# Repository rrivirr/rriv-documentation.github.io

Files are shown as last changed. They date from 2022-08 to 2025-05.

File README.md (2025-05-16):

# RRIV Documentation

### Introduction

RRIV is an open system for logging environmental data.

### Getting Started

* [Quick Start](quick_start.md)

### Organization

* [Goals](goals/)
* [Community](community/)
* [Licenses](licenses/)
* [Tools](organization/tools/)
* [Security](organization/security.md)

### Environmental Monitoring System

#### Platform

* [System Principles](principles/)
* [Features](features/)
* [Command Line Interface](cli/)

#### Applications

* [Build](build/)
* [Hardware Library](hardware-library/)
* [Kits](kits/)

### Engineering Organization

#### Development

* [Contributing](contributing/)
* [Roadmap](roadmap/)

#### System Documentation

* [Software Documentation](software/)
* [Hardware Documentation](hardware/)
* [Integrating Sensors and Actuators](integrating/)
* [Cloud](software/cloud.md)
* [Security](software/security.md)

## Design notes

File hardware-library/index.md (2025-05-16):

# Hardware Library

## Overview

The RRIV hardware library collects informations about various datalogger and sensor hardware that may be useful for specific environmental sensing use cases. TThird party sensors and other components may be easily integrated into the RRIV datalogger, and this library provides information to encourage that use. Documentation may also suggest particular sensor models, but these should not be interpreted as endorsements.

It is up to you to verify that any third party sensor or component will perform correctly for your specific deployment goals. Thus RRIV explicitly does not provide any warranty or guarentee for any third party hardware listed or suggested for use in our documentation.

Submissions to this hardware library are encouraged, and can be submitted as pull requests to this repository, located at https://github.com/rrivirr/rriv-documentation

## Sensors

* [Temperature](temperature/)
* [Conductivity](conductivity/)
* [pH](pH/)
* [Humidity](humidity/)
* [Color RGB](rgb/)
* [CO2](CO2/)
* [Methane](CO/)
* [CH4](ch4.md)

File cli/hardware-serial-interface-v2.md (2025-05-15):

# Hardware Serial Interface

## Overview

Command documentation conventions:

* \<required>
* \[optional]
* {...} json blob

RRIV compatible devices are configured using declarative commands as

`<command> <object> {key: value, key:value}`

or

`{command: <command>, object: <object>, key: value, key: value}`

Commands common to most objects are as follows:

### set

Creates or updates a resource.

### get

Gets current parameters of a resource, in a machine readable format.

### rm

Removes a resource

### reset

Resets parameters of an object back to defaults. Can accept a property to focus reset on that property.

### ls

Lists all resources of a particular tyle, in a tabular human readable format. This is not part of the standard, but implemented for ease of development. rrivctl does support this command, but by calling `get` and filtering the results down to a human readable format.

Consider if ls should be an abbreivate response for telemetry reasons, as in an index of objects without full properties.

### calibrate

Any object can potentially support a calibration routine

### run

Custom actions

\

## Commands

### Datalogger

Configurate data logger timing and metadata.

#### set datalogger {...}

{...} is JSON blob tha contains one or more datalogger parameter variables

```
{	
	"logger_name":"my device",
	"site_name":"OAK2:,
	"deployment_identifier":"X12",
	"interval": 10,
	"burst_number": 10,
	"start_up_delay": 1,
	"burst_delay": 2,
	"user_note": "none",
	"user_value": 12
}
```

| Parameter              | Data Type | Description                                                          |
| ---------------------- | --------- | -------------------------------------------------------------------- |
| logger\_name           | string    | a name for the logger                                                |
| site\_name             | string    | site code                                                            |
| deployment\_identifier | string    | identify a deployment                                                |
| wake\_interval         | int       | minutes between wakes while deployed                                 |
| warm\_up\_delay        | int       | minutes to wait between wakeup and measurement sensor initialization |
| burst\_interval        | int       | minutes between burst cycle initialization                           |
| user\_note             | string    | a note to add to each reading                                        |
| user\_value            | int       | a value to add to each reading                                       |

#### get datalogger \[{property: $property}]

* get datalogger \[property]

{command: get, object: datalogger, parameter: \<parameter>}

Get datalogger configuration. When called with a parameter argument, returns just the parameter requested. Otherwise returns the entire JSON blob.

#### reset datalogger \[{property: $property}]

* reset datalogger \[property]

Resets datalogger to factory default configuration, or just resets a particular property.

#### set datalogger {mode: \<mode\_request>, ...}

Changes the mode the datalogger is in

| Mode Request                               | Description                                                                                                       |
| ------------------------------------------ | ----------------------------------------------------------------------------------------------------------------- |
| interactive                                | Moves to interactive mode, which allows configuration                                                             |
| bench                                      | Moves to bench mode, which adds continuous serial output of measurements in addition to interactive mode features |
| deploy                                     | Moves immediately to deployment, sleeps the devices and awaits the next measurement cycle                         |
| deploy \<timestamp>                        | Moves to wait mode and sleeps the device. When timestamp is reached, the device wakes and deploys                 |

Datalogger also supports a shorthand which is outside the standard for mode switching over direct serial\
connection:

```
mode <mode_request>
```

\
\### Sensor

Commands to configure installed sensors.

#### set sensor \<id> {...}

Creates or updates a sensor configuration. If a sensor with the provided id is currently configured, it is updated. Otherwise, a new sensor configuration is created.

The JSON blob can contain some or all configuration parameters for indicated sensor driver. "type" specifies the kind of sensor installed and its corresponding driver, and is required when creating a new sensor.

Example (for generic analog sensor):

```
{	
	"type":"generic_analog",
	"burst_size":10,
	"adc_select":"internal",
	"sensor_port":1,
}
```

#### get sensor \[id] \[{property: }]

* rrivctl shorthand get sensor \[id] \[property]

Get a sensor configuration, corresponding to the id. When called with a parameter argument, returns just the parameter requested. Otherwise returns the entire JSON blob.

If id is not specified, returns a JSON array containing all sensor configurations.

get sensor also supports an aggregate property 'calibration' which returns all calibration parameters only

```
{
	'high_val': 5,
	'low_val': 2,
	'high_read': 2000,
	'low_read' : 300,
	'm': 2,
	'b': 0.2
}
```

#### rm sensor \<id>

Remove the sensor configuration matching the corresponding id

#### ls sensor

List all configured sensors in a tabluar format

#### calibrate sensor \<id> {action: $action, ...}

**action: point**

&#x20; Sets a calibration point

&#x20;`calibrate sensor <id> point {point: \$point_value, tag: $tag}`

**action: list, ls**

&#x20; Lists all the calibration points currently registered

&#x20;`calibrate sensor <id> list`

**action: remove, rm**

&#x20; Removes a registered calilbration point

&#x20;`calibrate sensor <id> remove {tag: $tag}`

**action: fit**

&#x20; Calculates fit based on calibration points that have been registered, and stores the fit.

&#x20;`calibrate sensor <id> fit { type: 'linear'}`

#### reset sensor {property: $property}

* reset sensor
* reset sensor {property: $property}
* reset sensor {property: 'calibration'}
* rrivctl shorthand: reset sensor $property

\
\### Actuator

Summary: actuator set, get, rm, ls

#### set actuator \[id] {...}

Creates or updates an actuator configuration. If an actuator with the provided id is currently configured, it is updated. Otherwise, a new sensor configuration is created.

#### get actuator \<id>

Get a actuator configuration, corresponding to the id. When called with a parameter argument, returns just the parameter requested. Otherwise returns the entire JSON blob.

If id is not specified, returns a JSON array containing all actuator configurations.

#### rm actuator \<id>

Remove the actuator configuration matching the corresponding id

#### ls actuator

List all configured actuators in a tabluar format

#### reset actuator {property: $property}

\
\### Telemeter

Summary: telemeter set, get, rm, ls

#### set telemeter \[id] {...}

Creates or updates an telemeter configuration. If an actuator with the provided id is currently configured, it is updated. Otherwise, a new sensor configuration is created.

#### get telemeter \<id> \[parameter]

Get a actuator configuration, corresponding to the id. When called with a parameter argument, returns just the parameter requested. Otherwise returns the entire JSON blob.

If id is not specified, returns a JSON array containing all telemeter configurations.

#### rm telemeter \<id>

Remove the telemeter configuration matching the corresponding id

#### ls telemeter

List all configured telemeters in a tabluar format

#### reset telemeter {property: $property}

\
\### Board\
The commands access features of the board itself and firmware metadata

This consists of three types of commands

* get/set commands in the standard that report hardware properties.
* warranty/license shorthands for human operators on the serial connection
* debugging shorthands for human developers on the serial connection

This is a custom namespace at the top level.

#### board version

```
get board { property: 'version'}
```

rrivctl: get board version

#### board firmware warranty

```
get board { property: 'firmware-warranty'}
get board { property: 'firmware'}
```

#### board firmware conditions

#### board firmware license

#### board rtc set \<epoch>

```
set board {'epoch': \$epoch} 
```

Set real time clock epoch time

#### board rtc get

Get the current real time clock epoch time stored on a RRIV device

```
get board { property: 'epoch'}
```

#### board restart

```
run board {'commmand' : 'restart'}
```

#### board i2c ls

#### board memory check

#### board mcu \[stop,sleep]

#### board signal \[high,low]

| Signal   | Description                        |
| -------- | ---------------------------------- |
| exADC    | enable/disable exADC               |
| 3v3Boost | enable/disable 3v3 boost converted |

\
\### Device\
Top level commands that dump and load all for the device in one payload

#### get

#### set

#### reset \<STM\_ID>

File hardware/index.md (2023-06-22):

# Hardware Documentation

## Overview

## Resources

* [Datasheets](datasheets/)
* [STLink Interface](board/programming-interface.md)

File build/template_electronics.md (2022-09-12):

# Electonics Build for ... 

## Bill of Materials

| Item        | Quantity    | Source URL  |
| ----------- | ----------- | ----------- |
| Waterbear   | 1           | https://... |
| Nucleao     | 1           | https://... |

## Schematics

Wiring diagrams.

## Build Process

### Tools & Skills

What's needed to build.

### Parts Fabrication

What to do with the bill of materials.

### Assembly & Waterproofing

How to put it together.

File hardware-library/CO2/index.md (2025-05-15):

# Carbon Dioxide (CO2) Sensors

## Background Science

* https://agupubs.onlinelibrary.wiley.com/doi/full/10.1002/2016RG000547

## Atlas Scientific CO2 Sensor

### Sensor Details

technology: optical\
range: 0-10000ppm +/-50ppm\

### RRIV Integration Details

driver: atlas\_co2\
case: developed\

### Product Links

* [Product page](index.md)

### Datasheets

* [Archived technical info 2023-07-07](index.md)

## MH-Z16

### Sensor Details

technology: NDIR\
range: 0-100000ppm\

### RRIV Integration Details

driver: under development\
case: under development\

### Product Links

* [Product page](https://sandboxelectronics.com/?product=100000ppm-mh-z16-ndir-co2-sensor-with-i2cuart-5v3-3v-interface-for-arduinoraspeberry-pi)
* [Datasheet](https://sandboxelectronics.com/wp-content/uploads/2018/08/Z16DS.pdf)

## Adafruit SCD41

### Sensor Details

technology: photoacoustic\
range: 400-5000ppm +/-50ppm\

### RRIV Integration Details

driver: not developed\
case: not developed\

### Product Links

* [Product page](https://www.adafruit.com/product/5190)

## Adafruit SCD30

### Sensor Details

technology: NDIR\
range: 400-10,000ppm +/-30ppm\

### RRIV Integration Details

driver: not developed\
case: not developed\

### Product Links

* [Product page](https://www.adafruit.com/product/4867)

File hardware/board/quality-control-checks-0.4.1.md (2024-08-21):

# Quality Control Checklist

## Checklist
* [pass] Powers up over USB
* [pass] Programmable
* [pass] Serial
* [pass] RGB LED
* [mod] Switchable power cycling
* [pass] 2.4V boost converter
* [pass] 3.3V boost converter
* [pass] 5V boost converter
* [pass] VIN measure
* [pass] intADC
* [pass] exADC
* [ ] I2C 3.3V
* [pass] I2C 5V
* [pass] exADC MOSFET
* [pass] Battery level MOSFET 
* [pass] intADC MOSFET
* [ ] Wake switch
* [mod] Voltage ORing VDD
* [pass] Voltage ORing 3.3V

## Noted Defects
* Orientation of reset button still wrong
  * Mitigation: remove reset button	
  * Alternate: may be possible to disconnect pads diagonally and get intended functionality
* Switchable power cycling resets on set low
  * Root cause: both ideal diodes are turning off at threshold
  * Mitigation: replace R21 with 357K
  * Fix: use mitigation or use ST pin on ideal diode for synchronized switching
* i2c hangs
  * this appears to be due to going low when 3v3 is switch off.
  * Fix: pullups should be agains VDD, not 3V3 

## Other Notes
* When VIN measure is disable, the ADC still reads a nonzero value
  * Suspect this is a floating voltage, test using current meter
* 5V boost has a very limited swing, around 100mV.  Still, the ripple pattern is spiky.  We could add a ferrite bead to smooth it.  This could go in the place of SB27 to feed the the exADC with smooth 5v.  To feed i2c we could place a bead in a similar solder bridge location.
* BOM included wrong pin count socket for J11 and J12

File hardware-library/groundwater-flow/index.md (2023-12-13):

# Data Sheets
* https://www.mouser.com/datasheet/2/609/max30210-3128806.pdf
* https://www.mouser.com/pdfDocs/max30210evkit.pdf
* https://www.analog.com/media/en/technical-documentation/data-sheets/4316fa.pdf

BOM
* https://www.ti.com/lit/ds/symlink/tps7a20.pdf?HQS=dis-dk-null-digikeymode-dsf-pf-null-wwe&ts=1702470498525

# Other Temperature Sensors
* https://www.te.com/usa-en/product-CAT-DTS0001.html
* https://www.harfington.com/products/p-1213532?currency=USD&variant=42565797216505&utm_medium=cpc&utm_source=google&utm_campaign=Google%20Shopping&stkn=f8e35277684b&utm_source=google&utm_medium=cpc&utm_campaign=1013-pmax-us-powerele8-&utm_term=1013-pmax-us-powerele8-&utm_content=ywh&gad_source=1&gclid=Cj0KCQiA35urBhDCARIsAOU7Qwlhizj8V51s7NARGC8W3OzX_mQPplGzPusJnYH1U20nPWnSQYRO4ssaAhsTEALw_wcB

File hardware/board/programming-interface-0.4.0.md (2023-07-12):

# Programming Interface

## Overview

This document details the programming interface for version 0.4.0 of the RRIV datalogger.  For version 0.4.1 and later, see [programming-interface.md]()

On version 0.4.0 of the RRIV datalogger, the ST-Link programming pins and serial interface pin are exposed in J5 and J6.  

These locations may have pin headers or JST XH size sockets installed, but either will accept Dupont connectors from the corresponding pins on the programming board.  This is the preferred way to interface with and program the MCU.

## Boards and Locations
### RRIV PCB
RRIV PCB

### RRIV PCB Layout
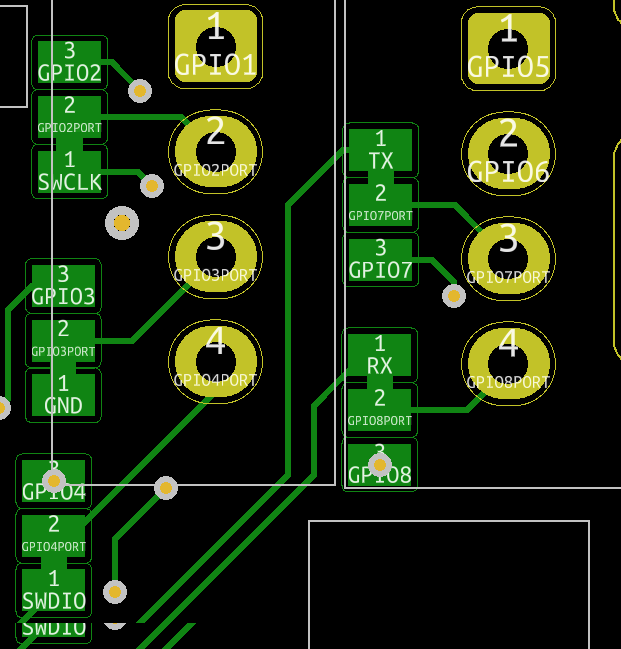
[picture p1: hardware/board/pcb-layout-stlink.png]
RRIV PCB Layout


### Programming Board
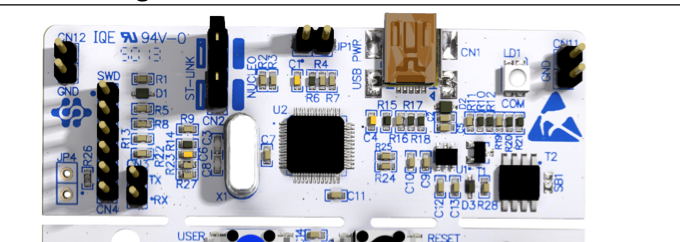
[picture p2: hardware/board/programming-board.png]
Programming Board


### Programming Board Detail
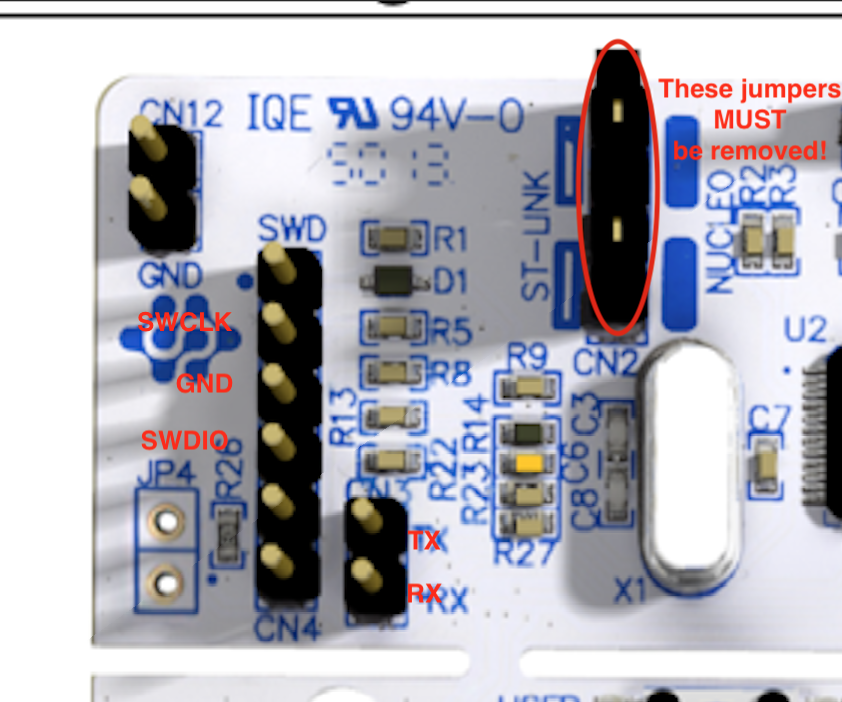
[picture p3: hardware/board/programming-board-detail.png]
Programming Board


### Programming Board Pinout
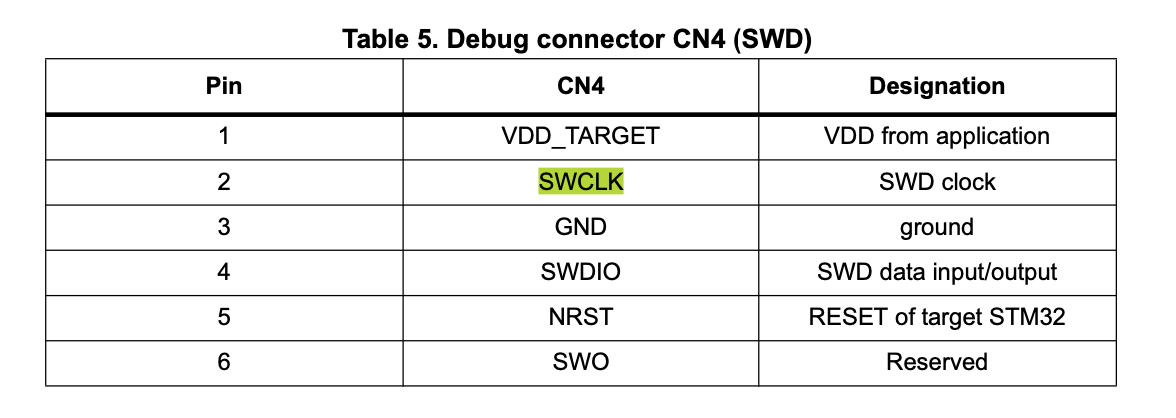
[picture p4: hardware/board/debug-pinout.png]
Programming Board


## Connecting the RRIV datalogger for programming

1. Connect SWCLK, GND, SWDIO, RX, and TX from the programming board ot the RRIV datalogger using Dupont female-female connectors
2. Ensure that both jumpers at CN2 on the programmer board are removed
2. Plug the USB port of the programming board into the computer using a USB cable.
3. Power the RRIV board, using a second USB cable into the RRIV datalogger's USB port. (v0.4.1 boards may also be powered by battery)
4. You may now program the RRIV datalogger and monitor serial using platformio.

## Notes
* The USB port on the RRIV datalogger currently in ONLY for supplying power to the board on the bench.  The RRIV datalogger cannot currently be programmed or interacted with thorugh this port.
* In some cases the MCU on the RRIV datalogger may need to be reset in order to program it.  The recommended path for this is to power cycle the board.

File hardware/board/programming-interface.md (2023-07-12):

# Programming Interface

## Overview

On version 0.4.1 and later of the RRIV datalogger, the ST-Link programming pins and serial interface pin are exposed in J5 and J6.  

These locations may have pin headers or JST XH size sockets installed, but either will accept Dupont connectors from the corresponding pins on the programming board.  This is the preferred way to interface with and program the MCU.

## Boards and Locations
### RRIV PCB
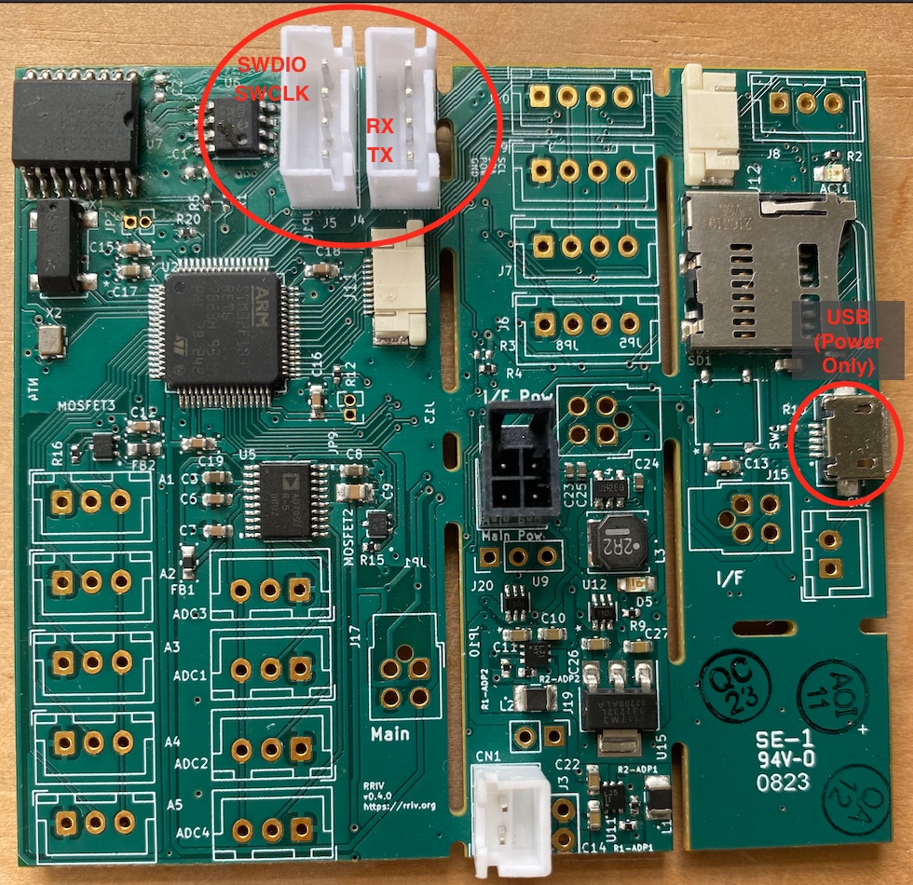
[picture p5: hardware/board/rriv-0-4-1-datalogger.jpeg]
RRIV PCB


### Programming Board
Programming Board

### Programming Board Detail
Programming Board

### Programming Board Pinout
Programming Board

## Connecting the RRIV datalogger for programming

1. Connect SWCLK, SWDIO, RX, and TX from the programming board ot the RRIV datalogger using Dupont female-female connectors
2. Power the board using USB. Generally if the board is powered by USB, it is not necessary to connect an additional ground cable between the programming board and the PCB
3. Ensure that both jumpers at CN2 on the programmer board are removed
4. Plug the USB port of the programming board into the computer using a USB cable.
5. Power the RRIV board, using a second USB cable into the RRIV datalogger's USB port. (v0.4.1 boards may also be powered by battery)
6. You may now program the RRIV datalogger and monitor serial using platformio.
7. If the board fails to program, the following two additional steps may help it get into programming mode
  1. Connect a Dupont cable between GND on the programmer one of the GND pins on the RRIV datalogger.  Typically you may use the GND pin on an open I2C socket.
  2. Press the reset button just before the board is programmed.  You may do this immediately before or immediately after pressing the 'run' button in platformIO.

## Notes
* The USB port on the RRIV datalogger currently in ONLY for supplying power to the board on the bench.  The RRIV datalogger cannot currently be programmed or interacted with through this port.
* In some cases the MCU on the RRIV datalogger may need to be reset in order to program it.  The recommended path for this is to power cycle the board.

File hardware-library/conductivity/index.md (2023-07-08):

# Electical Conducitivity Sensors

## Atlac EC Sensor

### RRIV Driver Details
driver: atlas_ec

### Product Links
* [Product page](https://www.google.com/url?sa=t&rct=j&q=&esrc=s&source=web&cd=&ved=2ahUKEwi30oOe7P3_AhVPJkQIHbI7B8wQjBB6BAgXEAE&url=https%3A%2F%2Fatlas-scientific.com%2Fkits%2Fconductivity-k-0-1-kit%2F&usg=AOvVaw3qBv8ugVFJyb1ZsS51Sytv&opi=89978449)

### Datasheets
* [Archived technical info 2023-07-07]()

## DIY EC Sensor
under development

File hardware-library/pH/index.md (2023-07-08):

# pH Sensors

## Gravity Analog ph Sensor

### RRIV Driver Details
driver: generic_analog

### Product Links
* [Product page](https://www.dfrobot.com/product-1782.html)
* [Product wiki](https://wiki.dfrobot.com/Gravity__Analog_pH_Sensor_Meter_Kit_V2_SKU_SEN0161-V2)

### Datasheets
* [Archived technical info 2023-07-07](Gravity__Analog_pH_Sensor_Meter_Kit_V2_SKU_SEN0161-V2-DFRobot.pdf)

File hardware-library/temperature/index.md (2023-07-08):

# Temperature Sensors

## Basic Analog Temperature Sensor (Thermistor)

This DIY implementation involves wiring a thermistor into a voltage divider to produce an analog sensor.

### RRIV Driver Details
driver: generic_analog

### Product Links

### Datasheets

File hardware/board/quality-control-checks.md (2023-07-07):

# Quality Control Checklist

[ ] Powers up over USB
[ ] RGB LED
[ ] 2.4V boost converter
[ ] 3.3V boost converter
[ ] 5V boost converter
[ ] Switchable power from battery
[ ] intADC
[ ] exADC
[ ] I2C 3.3V
[ ] I2C 5V
[ ] exADC MOSFET
[ ] Battery level MOSFET 
[ ] intADC MOSFET
[ ] Wake switch

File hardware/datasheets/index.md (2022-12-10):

# Datasheets

## Overview

This folder contains datasheets for components of the WaterBear and RRIV PCBs

## Datasheets
* [F103RB MCU](stm32f103rb.pdf)
* [F103RB MCU Reference Manual.pdf](STM32F10xxx%20Reference%20Manual.pdf)
* [EEPROM](24AA08-24LC08B-24FC08-8K-I2C-Serial-EEPROM-20001710N.pdf)
* [External ADC](AD7091R-5.pdf)
* [Boost Converter](ADP1606_ADP1607.pdf)
* [RGB LED](APHF1608LSEEQBDZGKC.pdf)
* [Realtime Clock](DS3231.pdf)
* [Nucleo User Manual](Nucleo64%20User%20Manual.pdf)
* [Nucleo Schematics](Nucleo%20F103RB%20Schematics.pdf)

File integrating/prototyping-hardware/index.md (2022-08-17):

# Recommended process for prototyping hardware

1. Design a strip based routing for the circuit
1. Layout circuit on breadboard
  * Connect nets using strip based routing
  * Use plugs to connect other components
1. Transfer circuit to stripboard for deployment

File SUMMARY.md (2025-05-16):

# Table of contents

* [RRIV Documentation](README.md)
* [Quick Start](quick_start.md)
* [applications](applications/README.md)
  * [DF Robot Analog pH Sensor](applications/dfrobot_ph_integration.md)
  * [GHG Bucket Flux Protocol](applications/ghg_flux_method.md)
* [build](build/README.md)
  * [Waterproof CO2 Sensor](build/co2_sensor.md)
  * [Electonics Build for R\&D Conductivity Sensor](build/conductivity_sensor_switching.md)
  * [Build](build/index.md)
  * [Methane and Carbon Dioxide Case](build/methane_case_1ft.md)
  * [GHG System Case](build/methane_case_2ft.md)
  * [Waterproof Methane Sensor](build/methane_sensor.md)
  * [Case Title](build/template_case.md)
  * [Electonics Build for ...](build/template_electronics.md)
  * [Sensor Title](build/template_sensor.md)
  * [applications](build/applications/README.md)
    * [RRIV Methane Beta Setup](build/applications/methane_beta_build.md)
  * [sensors](build/sensors/README.md)
    * [DF Robot Analog pH Sensor](build/sensors/dfrobot_ph_integration.md)
* [cli](cli/README.md)
  * [CLI commands](cli/CLI_commands_v1.md)
  * [RRIVCTL Sugars](<cli/RRIVCTL Sugars.md>)
  * [Hardware Serial Interface](cli/hardware-serial-interface-v2.md)
  * [Thermistor Ring Protocols](cli/thermistor_ring.md)
* [hardware-library](hardware-library/README.md)
  * [Hardware Library](hardware-library/index.md)
  * [CO2](hardware-library/co2/README.md)
    * [Carbon Dioxide (CO2) Sensors](hardware-library/CO2/index.md)
  * [conductivity](hardware-library/conductivity/README.md)
    * [Electical Conducitivity Sensors](hardware-library/conductivity/index.md)
  * [groundwater-flow](hardware-library/groundwater-flow/README.md)
    * [index](hardware-library/groundwater-flow/index.md)
  * [pH](hardware-library/ph/README.md)
    * [pH Sensors](hardware-library/pH/index.md)
  * [temperature](hardware-library/temperature/README.md)
    * [Temperature Sensors](hardware-library/temperature/index.md)
  * [CH4](hardware-library/ch4.md)
* [hardware](hardware/README.md)
  * [Hardware Documentation](hardware/index.md)
  * [board](hardware/board/README.md)
    * [Programming Interface](hardware/board/programming-interface-0.4.0.md)
    * [Programming Interface](hardware/board/programming-interface.md)
    * [Quality Control Checklist](hardware/board/quality-control-checks-0.4.1.md)
    * [Quality Control Checklist](hardware/board/quality-control-checks-template.md)
    * [Quality Control Checklist](hardware/board/quality-control-checks.md)
  * [datasheets](hardware/datasheets/README.md)
    * [Datasheets](hardware/datasheets/index.md)
* [integrating](integrating/README.md)
  * [Integrating](integrating/index.md)
  * [adding-driver](integrating/adding-driver/README.md)
    * [Driver integration steps](integrating/adding-driver/index.md)
    * [Steps](integrating/adding-driver/steps.md)
  * [prototyping-hardware](integrating/prototyping-hardware/README.md)
    * [Recommended process for prototyping hardware](integrating/prototyping-hardware/index.md)
* [roadmap](roadmap/README.md)
  * [Development Roadmap](roadmap/index.md)
* [software](software/README.md)
  * [branch-and-commit-methodology](software/branch-and-commit-methodology.md)
  * [repository-structure](software/repository-structure.md)
  * [security](software/security.md)
  * [cloud](software/cloud.md)
* [Organization](organization/README.md)
  * [Goals](goals/README.md)
  * [Community](organization/community/README.md)
    * [Community Roadmap](community/community.md)
    * [Community](community/index.md)
    * [Organization Chart](community/organization_chart.md)
  * [Security](organization/security.md)
  * [Tools](organization/tools/README.md)
    * [Joplin Notes](organization/tools/joplin-notes.md)

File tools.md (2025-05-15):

# Tools

## Project Tools

There are two classes of users

* directors?
* member
  * Members get @rriv.org addresses
* contributor
  * Contributors use their free proton account addresses
  * ( or their own personal email addresses (with less access to stuff) )

Calendar, drive, docs, and password manager shall all be handled via Proton services.\
Users without paid accounts shall create a free proton accoun to access Proton services.\
The main calendar will be the RRIV proton calendar

If organizational email filtering becomes desirable, we can use filtering functionality in Proton for Organizations\
https://proton.me/support/filter-lists-organization

Chat and video conferencing shall be handled via Matrix (element, jitsi)

Our IDP shall be keycloack running in our own cluster

### Documentation and Notes

We shall use Joplin for sharing notes between developers

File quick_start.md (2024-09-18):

# Quick Start

There are two kinds of roles available when using the RRIV platform.  
One is contributing as a developer, this means writing code and uploading this
code to the RRIV board to make new functionality.
The other is operating the board to develop new sensors or deploy them into the field. 
This role is called being an operator.

This quick start guide is divided into setup paths for either developer or operator roles.  
A developer probably wants to do both setups, while an operator only needs to set up for the 
operator role.

Choose the right setup path for your use case below and get started!

## Operator Setup

To get set up to operate and deploy the RRIV board, you will need to install the rrivctl command line
tool and set up your computer for USB communication with the RRIV board.   You will communicate
with the RRIV board using the rrivctl command line tool.

The instructions below are for linux.  If you are using MacOS or Windows some of the installation steps
will be different.

1. Download and install the rrivctl command line tool
   1. Navigate to https://github.com/rrivirr/rriv-ctl
   2. Clone this repository onto your computer using git
   3. Using the command line, navigate to the rriv-ctl folder
   4. Install nodejs dependencies on your computer
      1. sudo apt-get install nodejs
      2. sudo apt-get install npm
      3. sudo npm i typescript -g
   5. Follow the setup instructions in rriv-ctl/README.md
      1. npm install # installs the nodejs packages required by rriv-ctl
      2. npm run build # builds the rriv-ctl tool
      3. source ./create-alias.sh # makes the command rrivctl available on the command line
      4. You can now test this installation by typing `rrivctl` on the command line, you should see the help message.
3. Update your computer to allow USB communication with the rriv board
   1.  The following two files must be copied into the /etc/udev/rules.d/ folder on your computer
      1.  [https://github.com/rrivirr/rriv-documentation/blob/main/hardware/udev/69-probe-rs.rules]()
      2.  [https://github.com/rrivirr/rriv-documentation/blob/main/hardware/udev/69-rriv.rules]()
   3. Download each file using the 'raw' link on github provided by the links above
   4. Copy them into place using a command like `sudo cp ${filename} /etc/udev/rules.d/`
   5. After both files are copied into place, reload the udev rules by running `sudo udevadm control --reload`
5. Now we can try connecting to the board
   1. Plug the RRIV board into the computer using the USB port.   
   2. Run the command `rrivctl connect`

## Developer Setup

To get set up to write new code for the rriv firmware and/or to install compiled firmware onto the RRIV board, it is necessary to set up the development environment.

1. Clone the rriv-rust repository
2. Install rust toolchain following the instructions in the readme here: https://github.com/rrivirr/rriv-rust
   1. Follow the instructions here to install rustup: https://rustup.rs/
   2. rustup toolchain install nightly
   3. rustup target add thumbv7m-none-eabi
   4. rustup default nightly
   5. cargo install probe-rs --features cli
3. Install VSCode
4. Install required VSCode extensions
   1. rust-analyzer
   2. probe-rs-debugger
6. Install udev rules
   1.  The following two files must be copied into the /etc/udev/rules.d/ folder on your computer
      1.  https://github.com/rrivirr/rriv-documentation/blob/main/hardware/udev/69-probe-rs.rules
      2.  https://github.com/rrivirr/rriv-documentation/blob/main/hardware/udev/69-rriv.rules
   2. Download each file using the 'raw' link on github provided by the links above
   3. Copy them into place using a command like `sudo cp ${filename} /etc/udev/rules.d/`
7. Connect the jtag board between the computer and the RRIV board.
8. Test build and install by pressing the play button in VSCode

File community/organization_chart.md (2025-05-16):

# Organization Chart

This organization chart is a work in progress, as we bootstrap our organizational structure and key contributors.

Typically contributors listed here have a leadership role or make significant, sustained contributions to the platfform.

## Directors

* Zaven Arra - Executive Director & Founder
* Jake Hosen - Director & Founder

## Engineering

### Leadership & Key Contributors

* Zaven Arra - Engineering Lead

### Embedded Software Team

### Hardware Team

TBD

### Configuration Client Team

* Matty Interrupt - Client Development Lead

### Mobile

( No mobile functionality currently scheduled )

### Cloud

( No cloud functionality currently scheduled )

## Operations & Communication

### Web Team

TBD

### Onboarding Team

TBD

### Documentation

TBD

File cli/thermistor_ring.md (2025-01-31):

# Thermistor Ring Protocols

## Thermistor Ring Calibration
* Thermistor ring outputs two sets of values: the raw °C values from the digital thermistors using the factory calibration and the calibrated values using the offset produced by calibration.

### Thermistor Ring Calibration Commands

1. Set the temperature<br>
```rrivctl sensor set RING01 -f configuration/ring_temprature.json```
2. Clear existing calibration<br>
```rivctl calibrate sensor RING01 clear```
3. Calibrate for a given point (here we are calibrating when the known temperature is 22.3°C)<br>
```rrivctl calibrate sensor RING01 point 22.3```
4. This command will list the current ring values<br>
```rivctl calibrate sensor RING01 list```
5. Now we apply the calibration data to our dataset.<br>
```rivctl calibrate sensor RING01 fit```
6. Now we can run the command below and we will see all the configs including the calibration.<br>
```rivctl sensor get RING01```

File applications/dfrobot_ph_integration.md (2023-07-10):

# DF Robot Analog pH Sensor

## Parts needed
* [DFRobot pH Sensor](https://www.dfrobot.com/product-1782.html).
* M20 IP67 Cable Gland (Supplier: [Elecdirect Dome Cap Cable Gland](https://www.elecdirect.com/cord-grips-strain-relief/cable-glands/dome-cap-cable-gland-m20-19-35-black-complete-with-o-ring-locknut)).
* Lithium Moly Grease (e.g., [Lucasoil Lithium Grease](https://www.amazon.com/Lucas-Oil-10533-Lithium-Grease/dp/B004X70LZA/ref=asc_df_B004X70LZA/?tag=hyprod-20&linkCode=df0&hvadid=312151168520&hvpos=&hvnetw=g&hvrand=12751387308192042965&hvpone=&hvptwo=&hvqmt=&hvdev=c&hvdvcmdl=&hvlocint=&hvlocphy=9011858&hvtargid=pla-364752123727&th=1).
* 22 AWG Hook-Up Wire ([hook-up wire spool set](https://www.adafruit.com/product/3175?gclid=Cj0KCQiA95aRBhCsARIsAC2xvfzUefNXaZgFmL8MpqskC52_lq_Huy3KYFDuIzKR2XJ_EnG1sNZSfuQaAtqzEALw_wcB)).
* [3-pin female JST PH connectors and crimp pins](https://www.amazon.com/CQRobot-Connector-Terminal-Industrial-Integrated/dp/B0731MZCGF?th=1).

## Hardware Integration
* A cable must be built or modified to provide connectivity between the RRIV board and the Gravity analog pH meter. A female 3-pin JST-PH plug should be used for the end connecting to the pH meter. If using a RRIV v0.3 board, a female 3-pin JST-PH plug should be used for the end connecting to the RRIV board. For a RRIV v0.4 board, a female 3-pin _JST-SH_ plug should be used.
* Note: the sequence of pins on the RRIV and pH meter boards differ (see Figure 1). Construction of the cable should should follow the details in Figure 2

Figure 1: Connecting Gravity analog sensors to the analog to digital converter (ADC) ports. A) RRIV V0.4 board with ADC interfaces indicated; B) Close-up of RRIV ADC interfaces indicating connection configuration; C) Glose up of Gravity pH meter interface. Note the sequence of pins for this connect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 Figure 1: Connecting Gravity analog sensors to the analog to digital converter (ADC) ports.

Figure 2: Connecting Gravity analog sensors to the analog to digital converter (ADC) ports with closeup views of the cables used for connecting. Figure 1: Connecting Gravity analog sensors to the analog to digital converter (ADC) ports.

## Application and CLI Use
### Initial Setup
* Works with the _generic_analog_driver_.
* The command `set-slot-config` is used to configure a sensor for use with the RRIV logger:
	* `slot` is a digital slot of data set aside in the EEPROM to hold a sensor configuration
	* `type` is what driver type occupies the slot, these can be found by looking in the registry.cpp and following the "\_TYPE\_STRING" definitions
	* `tag` is a 5 character prefix for column headers, these should be left alone unless there are multiple of the same sensor in a system
	* `burst_size` is the number of reading cycles that should occur per burst
	* `sensor_pin` only for DHT22 currently, indicates which specific GPIO pin is being used for the sensor
	* `adc_select` only for analog sensors, can be either 'internal' or 'external' and indicates whether the analog sensor data is being processed by the ADC in the MCU or the external one
	* `sensor_port` only for analog sensors, indicates which physical port the sensor is occupying
* These can and should be used as they are to setup the AHT, CO2, and CH4 sensors, though once configured should be retained:
```
  set-slot-config {"slot":1, "type":"generic_analog", "tag":"pH", "burst_size":10, "adc_select":"external", "sensor_port":2}
```
* `get-config` is used to check the configuration of the settings as they are, the first section displayed is the datalogger settings followed by sensor slot settings
* The command `set-config` is used to configure sensors and sampling parameters.
	* `loggerName` is a colloquial name that has been written on the back of the board in sharpie
	* `siteName` is a 7 character string to indicate where the RRIV is being deployed, this will also be used in the folder structure of CSV output, so should be unique
	* `deploymentIdentifier` is a 15 character string to indicate what experiment is being run
	* `wakeInterval` is in minutes and determines when the board wakes up to begin measurement cycles. 60 indicates to wake up every hour, 1 indicates every minute. The next interval is calculated at the end of a measurement cycle
	* `startUpDelay` is a duration in minutes to delay before starting the measurement cycle
	* `burstNumber` indicates how many burst cycles to complete during a measurement cycle
	* `interBurstDelay` now also works as an interval given in minutes for when to begin taking readings. 1 indicates to take readings at every minute
* example of set-config that can be further customized. This command sets up a logger named "writeOnBoard" that will wake up after sleeping for 1 minute with 
```
set-config {"loggerName":"writeOnBoard", "siteName":"7char", "deploymentIdentifier":"15char", "wakeInterval":1, "startUpDelay":0, "burstNumber":60, "interBurstDelay":1}
```
* To check that all sensors are working properly use `start-logging`. This will display sensor readings at continuous intervals. You can evaluate the readings to confirm the sensor is operating properly. When you are done with this process type the command `stop-logging`. Data will continue logging so the keystrokes you type may become separated, but the command will register if you type the entire command and press enter. The data can be offloaded from the SD card to confirm that data collection was satisfactory.

### pH sensor calibration
* Calibration values are entered manually.
* Begin by typing the command `start-logging`. This will provide a continuous read of raw pH values in millivolts.
* While the sensor is logging, place hte sensor in the first calibration solution.
  * Once the raw voltage measurements have stabilized, record the pH of the calibration solution and the corresponding millivolt value of the sensor.
* Repeat the above step for one or two different other pH calibration solutions.
* Use the `calibrate` command to record the calibration values for the sensor. Each calibration point is entered with the following command, which has three values associated with it.
  * <calibrate> [sensor slot #] [step] [value]
  * The first value, `sensor slot #`, is the slot number previously assigned (in this example slot 1 was used).
  * The second value, `step`, is the pH of the calibration solution.
  * The third value, `value`, is the raw analog reading in millivolts obtained by the sensor.
* Repeat the step above for all 3 calibration points.

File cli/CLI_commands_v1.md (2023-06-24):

# CLI commands

## Overview

Command structure:
* `<command> [arguments]`

## Commands
### `<help>`
List all commands

### `<show-warranty>`
Display warranty information

### `<show-conditions>`
Display licensing information

### `<get-config>`
List the general datalogger settings followed by each slot configuration

### `<set-config> [JSON]`
Set the general datalogger configuration using a JSON which includes:
```
{
  "loggerName":[7 characters],
  "siteName":[7 characters],
  "deploymentIdentifier":[15 characters],
  "wakeInterval":[value in minutes],
  "startUpDelay":[value in minutes],
  "burstCycle":[value],
  "interBurstDelay":[value in minutes]
}
```
Example:
`set-config {"loggerName":"CAL3","siteName":"bucket3","deploymentIdentifier":"cold-cal1.3","wakeInterval":1,"startUpDelay":0,"burstNumber":60,"interBurstDelay":1}`

### `<set-slot-config> [JSON]`
Set the slot configuration, all slots have:
```
{
  "slot":[value],
  "type":[sensor type],
  "tag":[5 characters],
  "warmup":[value in seconds],
  "readingCycle":[value]
}
```
Additional items may be added depending on sensor type, current sensor types:
* generic_analog
* atlas_ec
* driver_template
* adafruit_dht22
* atlas_co2
* BME280
* adafruit_ahtx0

### `<clear-slot> [slot #]`
Clear the slot configuration for a specific slot #, number of slots is determined by size of EEPROM and value set for `EEPROM_TOTAL_SENSOR_SLOTS` in system/eeprom.h

### `<get-rtc>`
Get the current time in epoch and ISO8601

### `<set-rtc> [epoch timestamp]`
Set the DS3231 real time clock value

### `<calibrate> [sensor slot #]`
#### `<calibrate> [sensor slot #] [step] [value]`
Calibration commands for a sensor slot, generic analog driver calibration steps are `low` and `high` for a two-point calibration resulting in a linear relationship y=mx+b

### `<set-user-note> [note]`
Populate userNote column in CSV, will continuously populate with `[note]` until `[note]` is replaced

### `<set-user-value> [value]`
Populate userValue column in CSV, will continuously populate with `[value]` until `[value]` is replaced

### `<start-logging>`
Beging serial output of reading samples from configured sensors, 1 reading every 2 seconds

### `<stop-logging>`
Stop serial output of sensor reading samples

### `<deploy-now>`
Switch to deployment mode--wake at next interval and begin measurement cycles until running out of power

### `<i>`
Switch to interactive mode for user input

### `<restart>`
Restart the firmware

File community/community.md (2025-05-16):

# Community Roadmap

This section enlists our goals to expand our developer and contributors community .

## Authors

* [@moezmustafa](https://www.github.com/moezmustafa)

## How can you do awesome work with us ?

👩‍💻 Look around and find typos in documentaion...

🧠 No-code contribuitons are real...

🤔 Feel free to raise your hand...

⚡️ Fun fact : Open-Source is for everyone ...

## Roadmap

* Add a main profile.md (a special file) to the project
* Write a contents list with links
* Add badges
* Rasie Good First Issues

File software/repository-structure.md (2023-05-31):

├── .cargo
│  └── config.toml # <- no `build.target`
├── .vscode
│  └── settings.json
├── Cargo.toml # <- outer Cargo workspace
├── cross
│  ├── .cargo
│  │  └── config.toml # <- build.target = thumbv7*-*
│  ├── lib
│  │  ├── Cargo.toml
│  │  └── src
│  ├── board
│  │  ├── Cargo.toml
│  │  └── src
│  ├── Cargo.toml # <- inner Cargo workspace
│  └── self-tests
│     ├── Cargo.toml
│     └── tests
├── host-target-tests
│  ├── Cargo.toml
│  └── tests
├── control-interface
│  ├── Cargo.toml
│  └── src
└── xtask
   ├── Cargo.toml
   └── src

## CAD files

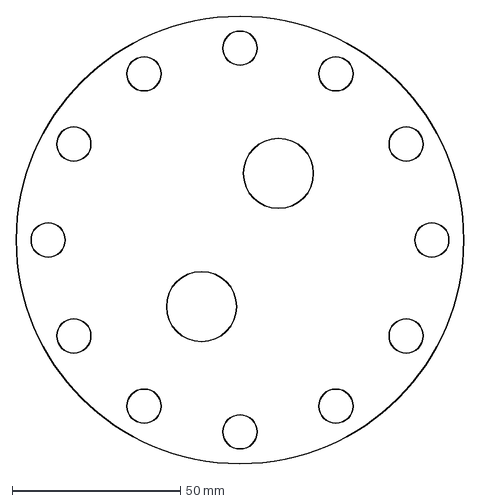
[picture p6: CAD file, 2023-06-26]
build/case/SensorPanel.dxf
133.0 x 133.0 mm

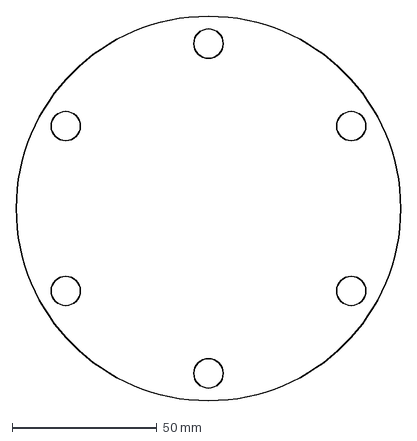
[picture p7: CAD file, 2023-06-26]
build/case/BackPanel.dxf
133.0 x 133.0 mm

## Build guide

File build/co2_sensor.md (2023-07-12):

# Waterproof CO2 Sensor
Sensor and waterproof case specifically for use with the Atlas EZO-CO2 sensor

## Bill of Materials

| Item                                                       | Case Qty   | Buy Qty   |  Supplier Part # / CAD link |
| ---------------------------------------------------------- | ---------- | --------- |  -------------------------- |
| Atlas Scientific EZO-CO2 sensor        | 1  | 1          | https://... |
| 1-1/4" PVC Sch 40         | 1 | 1 | |
| 1-1/4" PVC Sch 40 End Cap | 1 | 1 | |
| 1-1/4" PVC Sch 40 Hub x Hub Coupler | 1 | 1 | |
| MiniPax Dessicant | 1 | | |
| .005" PTFE film 6" Wide | Consumable | | |
| 8" cable tie | 2 | | |
| Solder | Consumable | | |
| Plastidip  | consumable | |
| Tall round cylinder container | | | |
| Epoxy | Consumable | | |
| Epoxy Putty | Consumable | | |
| RDC13NR Cord Grip | 1 | | |
| Jst-PH 4pin plug | 1 | | |
| Dupont 1pin socket plug | 1 | | |

## Schematics

Wiring diagrams.

### Communication protocol

### Power solution

## Diagrams

Mechanical drawings.

## Build Process

### Tools & Skills

Drill
1/4" drill bit
Ridgid Quick-acting tubing cutter (model 151)
Deburring tool (find the right sized one for 1-1/4" pvc)
Scalpel / art knife
Wire stripper
Wire cutter
Dupont Crimping Pliers
Engineer PA-21 Crimping Pliers
Soldering iron
Gloves
Fume hood / well ventilated area
Tension rod (for fume hood)
Shower rings & clips

### Parts Fabrication

1. Cut PTFE film to 3" x 3" square
2. Drill 1/4" hole in center of cap
3. Cut PVC to 2.25" and deburr both ends, until they are smooth to touch (only have to do one end if you keep track of it as the end that contacts the PTFE)
4. Drill two offset rings of 8x 1/4" holes in the bottom half of PVC coupler (can do 4 holes if you drill all the way across)
5. Cut CO2 cable down to 8.5"

### Assembly & Waterproofing

1. Thread sensor cable through the cap
2. Strip 1" off cable, and 2mm off each wire, then crimp and add JST-PH connector and Dupont connector
3. Test that the sensor still works, if not, check wiring or switching to I2C mode, once it works, use a scalpel/art knife to lift the tabs holding connectors from step 2 in place, and remove them
4. Sandwich 3"x3" square of PTFE film between 1.5" PVC section and end of PVC coupler without holes, carefully compress the parts as far as possible.  If you hear a tearing sound, start over with new PTFE
5. Add interlock two zipties and place around the coupler over the set of holes closest to the bottom
6. Add a small amount of Epoxy putty to block the whole in the cap around the cable, it might help to hold it upside down when pushing the putty into the gap slightly, so the cable does not move around as much
7. Add Epoxy around seam between PVC cap and coupler, or mainly the seam from those two components to the PVC pipe section
8. Let both Epoxy and Epoxy putty cure for 1 hour, hanging upside down using the zipties and shower ring clips in the fume hood or well ventilated space
9. Fill cylinder container with Plastidip and mix thoroughly
10. Use masking tape to cover the exposed wires and crimps in a tube
11. Slowly insert and extract masking tape side first into Plastidip filled container (1" every 5 seconds), taking care to evenly coat each area.  Dip up to ~1" of the coupler, not covering the drilled holes, hang to cure for 30 min, and apply a second coating
12. After 30 min, inspect for any gaps that can be filled using a spatula, taking care not to create bubbles
13. Hang to cure for 8 hours in ventilated space, and inspect and fill gaps as necessary
14. Remove the zip ties, remove around 4.5" of the Plastidip around the cable and masking tape, carefully use a cutting tool and the wire stripper to do this
15. Remove the masking tape, then add the cable grip on over the plastidipped section, and place the connectors back on the wires
16. Test the sensor is working correctly, if i2c errors are shown then try manually switching the CO2 sensor to I2C mode by powering on the device with blue and green wire shorted together for a few seconds

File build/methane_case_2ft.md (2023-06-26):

# GHG System Case

Case specifically for use with the Figaro NGM2611-E13, Adafruit DHT22, AtlasScientific EZO-CO2 sensor, and 6 D cell batteries.  Which informs the sensor plate, cable glands, and power supply (length of case and nylon bar).
[TODO: If we removed / generalized the sensor plate and cable glands requirements / instructions this could generally be for a 12" elongated case]: #

## Bill of Materials and Potential Supplier or Drawing

[columns? availability, manufacturer part number, manufacturer, notes]: #
[comment test]: #

| Item                                                       | Case Qty   | Buy Qty   |  Supplier Part # / CAD link |
| ---------------------------------------------------------- | ---------- | --------- |  -------------------------- |
| 3" ABS Schedule 40 Pipe                                    | 12"        | 10'       | [Menards 6881155 ](https://www.menards.com/main/plumbing/pipe-fittings/abs-pipe-fittings/10-abs-sch-40-plain-end-cellular-core-dwv-pipe/abs033000600hc/p-1444426392509-c-8562.htm) |
| 3" ABS Hub x Hub Coupler                                   | 2          | 1         | [Menards 6881537 ](https://www.menards.com/main/plumbing/pipe-fittings/abs-pipe-fittings/nibco-reg-hub-abs-dwv-coupling/i00975h/p-1444449159767-c-8562.htm) |
| -341 EPDM 70A O-ring                                       | 2          | 15        | [McMaster-Carr 9557K316](https://www.mcmaster.com/9557K316/) |
| 18-8 Stainless Steel Threaded Rod 3/8" -16                 | 6          | 2'        | [McMaster-Carr 98804A031](https://www.mcmaster.com/98804A031/) |
| 18-8 Stainless Steel Hex Nuts 3/8" -16                     | 24         | 100       | [McMaster-Carr 91845A031](https://www.mcmaster.com/91845A031/) |
| 18-8 Stainless Steel Washers 3/8"                          | 24         | 100       | [McMaster-Carr 92141A031](https://www.mcmaster.com/92141A031/) |
| 5" Copper Mesh/Gauze                                       | 20"        | 100'      | [McMaster-Carr 6361T16 ](https://www.mcmaster.com/6361T16/) |
| Dow Corning 111 Molykote                                   | Consumable | 5.3 Fl oz | [McMaster-Carr 1204K32](https://www.mcmaster.com/1204K32/) |
| Dessicant Packet                                           | 1          | 1000      | [McMaster-Carr 2189K34](https://www.mcmaster.com/2189K34/) |
| 11" Cable Ties                                             | 4          | 100       | [McMaster-Carr 7130K55](https://www.mcmaster.com/7130K55/) |
| Dome Cap Cable Gland 1/2" NPT .19-.35" w/ O-Ring & Locknut | 2          | 1         | [elecDirect RDC13NR](https://www.elecdirect.com/cord-grips-strain-relief/cable-glands/dome-cap-cable-gland-1-2-npt-19-35-black-complete-with-o-ring-locknut) |
| 3/4" wide Velcro                                           | 1"         | 5'        | [McMaster-Carr 9273K13-9273K133](https://www.mcmaster.com/9273K13-9273K133/) |
| 18-8 Stainless Steel Phillips Flat Head #6 x 1/2" Screws   | 6          | 100       | [McMaster-Carr 90065A148](https://www.mcmaster.com/90065A148/) |
| 3/4" x 3/4" Nylon Bar                                      | 1'         | 1'        | [McMaster-Carr 8732K17](https://www.mcmaster.com/8732K17/) |
| 1/4" Clear Acrylic Lid Plate*                              | 1          | NA        | [CAD Drawing 3inch](https://github.com/rrivirr/sonde/tree/master/panels) |
| 1/4" Clear Acrylic Sensor Plate*                           | 1          | NA        | [CAD Drawing 3inch](https://github.com/rrivirr/sonde/tree/master/panels) |
| 1/4" Clear Acrylic Cage Plate*                             | 1          | NA        | [CAD Drawing 3inch](https://github.com/rrivirr/sonde/tree/master/panels) |
| ABS Cement                                                 | Consumable | NA        | [Menards  6932185](https://www.menards.com/main/plumbing/plumbing-installation-repair/pipe-cements-cleaners-primers/oatey-reg-medium-black-abs-cement-4-oz/309995/p-1444449932067-c-8530.htm?tid=-7621218153408053791&ipos=1) |
| 2D cell battery holder with center mounting points | 3 | 1 | [MPJA 36651 BH](https://www.mpja.com/Battery-Holder-2-D-Cell-Series/productinfo/36651%20BH/) |

*[Send Cut Send](https://sendcutsend.com/)

## Diagrams

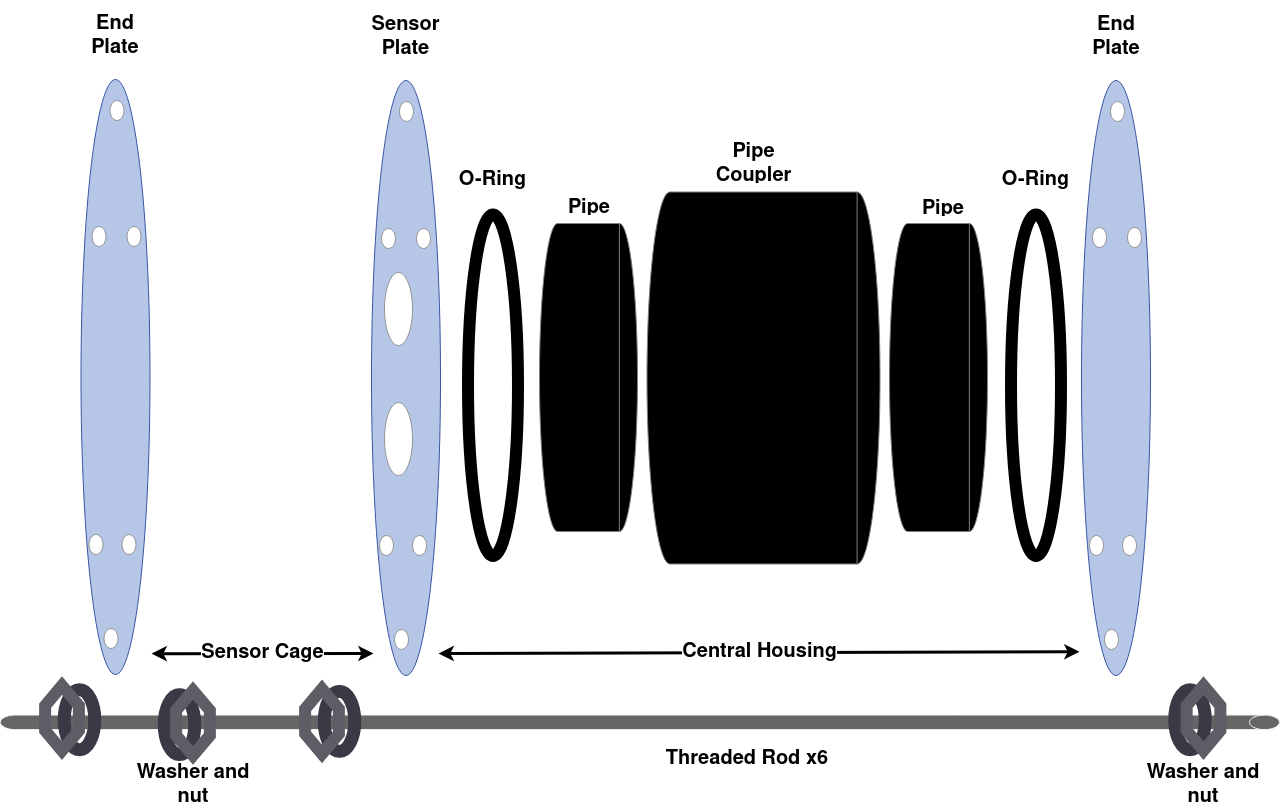
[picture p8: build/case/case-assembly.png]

Fig. 1 : Annotated Case Diagram

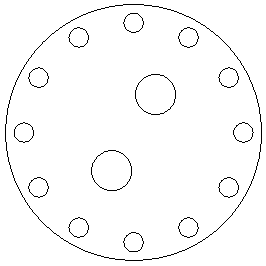
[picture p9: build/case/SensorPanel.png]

Fig. 2 : Sensor Panel

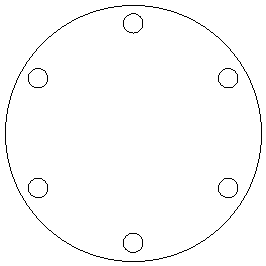
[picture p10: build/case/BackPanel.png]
s

Fig. 3 : Back and Cage Panel

## Build Process

### Tools & Skills
#### Fabrication

- [Reed TC4QP Tubing Cutter for plastic pipe](https://www.reedmfgco.com/en/products/plastic-pipe-tools/quick-release-tubing-cutters-for-plastic-pipe/tc4qp/) to cut ABS to length
- Measuring tape
- #2 phillips head screw driver 
- Power drill and 1/4" drill bit

#### Assembly
- 2x [9/16 SAE combination wrench](https://www.mcmaster.com/56255A34/) for hex nuts
- [Milwaukee 6in Diagonal Cutting Pliers](https://www.milwaukeetool.com/Products/Hand-Tools/Pliers/Diagonal-Cutters/48-22-6106) for copper mesh and cable ties

### Parts Fabrication

- Cut two 1-21/32" length sections of ABS and 1x 8-1/4" length for the hub inserts and main housing section. When making hub inserts, 20/32 to 22/32 is acceptable, too little won't hold the o-ring in place, too much won't compress the o-ring enough to seal properly. 
  - these lengths may vary depending on brand of coupler, length to cut the ABS sections the O-rings will go around are based on compressing the O-ring around 25% of it's width of 0.21" = 0.1575"  or ~5/32"
  - for the NIBCO brand coupler we found a depth of 1 1/2", so 1 1/2" + 5/32" = 1 21/32"
  - we also found the center barrier in the coupler is measured at around 1/4", 1 21/32" + 1/4 = 1 29/32", 12" - 2x 1 29/32" = ~8 1/4"
- Mark placement of battery holder screw placements on Nylon bar
- Drill 3/32" pilot holes into nylon bar (for #6 screws) according to battery holder placement centered on bar, then screw battery holder into nylon bar
- Cut 20" of copper mesh

### Assembly & Waterproofing

1. Attach cable glands 
	1. Apply a small amount of molycote to O-Ring on each cable gland
	2. Fit cable glands through their respective holes in acrylic sensor plate
	3. Tighten plastic nut on cable gland gently but firmly to ensure waterproof seal
2. Assemble main sonde housing (ABS or PVC)
	1. Assemble O-Ring ledge
		1. Find 2 3" pipe D-couplers and 2 1-21/32" sections of 3" pipe
		2. Apply plastic cement primer to one end of each D-coupler and one end of each pipe section
		3. Apply plastic cement to primed end of D-coupler.
		4. Insert primed end of each pipe section into primed and cemented end of each D-coupler
		5. Tap with rubber mallet to ensure complete insertion, and visually check that that there is no gab between the 1-21/32" pipe section and the insertion ridge inside the D-coupler.  This is essential to ensure the correct ledge height for the O-Ring.
		6. Check O-ring ledge assembly for correct height.
			1. Place an O-ring on the ledge created by the inner pipe inserted into the D-coupler in the above steps
			2. Check that at least 1.5mm of relief exists between the O-ring and the inner pipe segment for the entire circumference of the O-ring.
			3. The typical reason for a defect at this stage is incomplete insertion of the inner pipe segment into the D-coupler, which can easily compromise waterproofing.
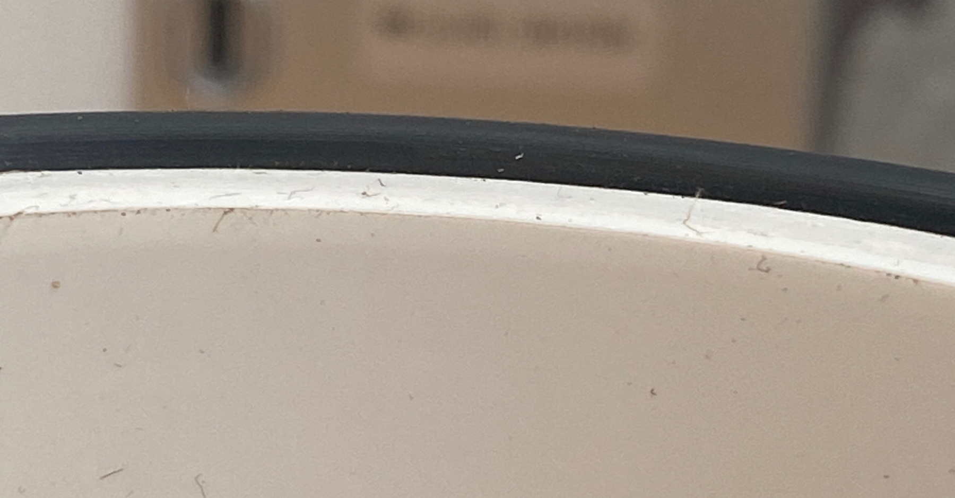
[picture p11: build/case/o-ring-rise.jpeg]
			4. Correct assembly results:  

	2. Assemble housing body
		1. Find 2ft length of 3" pipe and 2 O-Ring ledge assembles from (i)
		2. Check O-ring ledge assembly for correct height
			1. Checking for a good seal on each O
		2. Apply plastic cement primer to open end of D-coupler on O-Ring ledge assembly and both ends of 2 ft pipe.
		3. Apply plastic cement to open and primed end of O-Ring ledge assembly
		4. Firmly insert primed 3" pipe ends into primed and cemented ends of the D-coupler on each O-Ring ledge assembly.
	3. Let cure for 3 hours

3. Build case
	1. Find 6 threaded steel rods, 24 bolts, 24 washers, 2 O-rings, one sensor  plate with cable glands attached, and 2 cage/back plates, and the housing body assembled in (2)
	2. Build starts from the cage side of the sonde case and proceeds to the back.
	3. For each hole in the cage plate, sandwich the plate between two washers and two nuts screwed onto the end of a threaded steel rod.
		1. Screw a nut about 1 inch onto the rod
		2. Slide a washer up to the nut
		3. Slide the cage plate onto the rod
		4. Slide a washer up to the cage plate
		5. Tighten a 2nd nut up to the cage plate.
		6. Repeat for each hole in the cage plate.
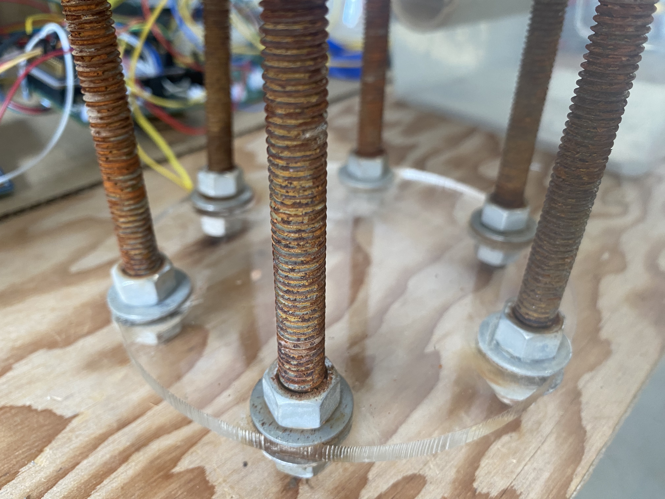
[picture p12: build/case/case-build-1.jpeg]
		7. Result looks like this: 
4. Next, use nuts and washers to create a ledge for the sensor plate to rest on.
	1. Stand the housing from (2) upright, and turn the assembly from (iii) upside down and place on top of the housing.  The cage plate will be facing upward.
	2. Mark each steel rod, using a marker or masking tape, 1 inch paste the height of the housing.  This will be the location of the ledge.
	3.  Take the assembly from (2) back off the housing and place cage plate side down on the table.
	4. Screw a nut onto each threaded rod up to the point that has been marked
	5. Place a washer on top of each nut
	6. Place the sensor plate onto the six rods and allow to rest on the 6 nuts and washers there just installed.
	7. Visually inspect that the sensor plate is reasonably flat and all six washers are at the same level.

5. Now, place O-rings and attach the back plate
	1. Place an O-ring on the O-ring ledge of one side of the housing from (2)
	1. Apply a thin layer of molykote to the entire surface of the O-ring
	1. Place the housing on the sensor plate and between the six rods, with the side with the installed O-ring facing down.
	1. Place a second O-ring on the O-ring ledge on the other side of the housing
	1. Apply a thin layer of molykote to the entire surface of the second O-ring
	1. Place the back plate onto the six rods
	2. Install a nut and washer onto each rod, and firmly screen them down onto the back plate.
	3. Check that all six sensor plate nuts are tight, and all six back plate nuts remain tight.  Tighten any nuts that appear to be loose.
	4. Visually inspect O-rings for any signs of improper compression
		1. Over-tightening: O-ring can squish out of place
		2. Under-tightening: O-ring is not in contact with acrylic plate in some location
6. Attach sensors (This step can also happen before step 5 with some experience doing assembly)
	1. Disassemble sonde case by removing the back panel, then the housing, then the sensor plate.
	2. Apply a thin layer of molykote to the inside of the cable glands
	3. Thread sensor cables (without connectors attached) through the cable glands
	4. Tighten cable glands to provide waterproof seal
	5. Reassemble sensor place, housing, and back plate onto the 6 steel rods as in (5)
	6. Assembly can now be dunk tested for waterproofness

6. Internal Assembly
	1. Ensure sonde case is disassembled
	1. Cut a 1" section of velcro.
	2. Attach velcro to back of RRIV datalogger PCA and open area on plastic rod
	3. Plug battery plug into RRIV datalogger
	4. Assemble sensor connectors
	4. Place batter/datalogger assembly upright on top of sensor plate.
	5. Plug sensors into datalogger
	6. Reassemble sonde case

8. Copper mesh
	1. Wrap copper mesh around sensor cage
	2. Secure copy mesh to sensor cage using zip ties

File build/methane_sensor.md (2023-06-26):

# Waterproof Methane Sensor

Sensor and waterproof case specifically for use with the Figaro NGM2611-E13, and Adafruit AHT20.

## Bill of Materials

| Item                                                       | Case Qty   | Buy Qty   |  Supplier Part # / CAD link |
| ---------------------------------------------------------- | ---------- | --------- |  -------------------------- |
| NGM2611-E13        | 1  | 1          | https://www.figarosensor.com/product/entry/ngm2611.html source w/ 2 month lead |
| AHT20              | 1  | 1           | https://www.adafruit.com/product/4566 |
| 1-1/4" PVC Sch 40         | 1 | 1 | |
| 1-1/4" PVC Sch 40 End Cap | 1 | 1 | |
| 1-1/4" PVC Sch 40 Hub x Hub Coupler | 1 | 1 | |
| 8 conductor cable* | 7.5" |1m | digikey |
| MiniPax Dessicant | 1 | | |
| .005" PTFE film 6" Wide | Consumable | | |
| 8" cable tie | 2 | | |
| Solder | Consumable | | |
| Plastidip  | consumable | |
| Tall round cylinder container | | | |
| Epoxy | Consumable | | |
| Epoxy Putty | Consumable | | |
| Protoboard/stripboard* | Consumable | | |
| Mini glue gun stick | Consumable | | |
| RDC13NR Cord Grip | 1 | | |
| Jst-PH 3pin plug | 3 | | |
| Dupont 1pin socket plug | 1 | | |
| Jst-XH 4pin socket* | 1 | | |
| Jst-XH 4pin plug* | 1 | | |

## Schematics

Wiring diagrams.

### Communication protocol

### Power solution

## Diagrams

Mechanical drawings.

## Build Process

### Tools & Skills

* Drill
* 1/4" drill bit
* Rigid Quick-acting tubing cutter (model 151)
* Deburring tool (find the right sized one for 1-1/4" pvc)
* Scalpel / art knife
* Wire stripper
* Wire cutter
* Dupont Crimping Pliers
* Engineer PA-21 Crimping Pliers
* Soldering iron
* Mini glue gun
* Gloves
* Fume hood / well ventilated area
* Tension rod (for fume hood)
* Shower rings & clips

### Parts Fabrication

1. Drill 1/4" hole in center of cap
1. Cut PVC to 2.25" and deburr both ends, until they are smooth to touch (only have to do one end if you keep track of it as the end that contacts the PTFE)
1. Drill two offset rings of 8x 1/4" holes in the bottom half of PVC coupler (can do 4 holes if you drill all the way across)
1. Solder DHT22 to proto board (4x4) w/ JST-XH 4pin socket, 10k ohm resistor
1. Cut cable to 8.5", strip 1" off one end, then 2mm off each wire attach crimps and slide into JST-XH 4pin plug and Dupont 5pin socket
1. Cut PTFE film to 3" x 3" square

### Assembly & Waterproofing

1. Thread cable through the cap, and attach sensors
2. Strip 4" off cable, and 2mm off each wire, then crimp and add JST-PH connectors and Dupont connector
3. Test that the sensors still work, if not, check wiring, if they do, use a scalpel/art knife to lift the tabs holding connectors from step 2 in place, and remove them
4. Sandwich 3"x3" square of PTFE film between 1.5" PVC section and end of PVC coupler without holes, carefully compress the parts as far as possible.  If you hear a tearing sound, start over with new PTFE
5. Use the glue gun to coat the exposed contacts on the bottoms of one or both sensors, then add the sensors and dessicant pack inside the cap to the top of the PVC section, compress as much as possible
6. Add interlock two zipties and place around the coupler over the set of holes closest to the bottom
7. Add a small amount of Epoxy putty to block the whole in the cap around the cable, it might help to hold it upside down when pushing the putty into the gap slightly, so the cable does not move around as much
8. Add Epoxy around seam between PVC cap and coupler, or mainly the seam from those two components to the PVC pipe section
9. Let both Epoxy and Epoxy putty cure for 1 hour, hanging upside down using the zipties and shower ring clips in the fume hood or well ventilated space
10. Fill cylinder container with Plastidip and mix thoroughly
11. Use masking tape to cover the exposed wires and crimps in a tube
12. Slowly insert and extract masking tape side first into Plastidip filled container (1" every 5 seconds), taking care to evenly coat each area.  Dip up to ~1" of the coupler, not covering the drilled holes, hang to cure for 30 min, and apply a second coating
13. After 30 min, inspect for any gaps that can be filled using a spatula, taking care not to create bubbles
14. Hang to cure for 8 hours in ventilated space, and inspect and fill gaps as necessary
15. Remove the zip ties, remove around 4.5" of the Plastidip around the cable and masking tape, carefully use a cutting tool and the wire stripper to do this
16. Remove the masking tape, then add the cable grip on over the plastidipped section, and place the connectors back on the wires
17. Test the sensors are working correctly, it's only possible to correct wiring issues at the external part without opening the case and essentially starting over.

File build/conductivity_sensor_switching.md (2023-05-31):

# Electonics Build for R&D Conductivity Sensor

## Bill of Materials

| Item        | Quantity    | Source URL  |
| ----------- | ----------- | ----------- |
| Waterbear   | 1           | https://... |
| Nucleo      | 1           | https://... |

We use a spare waterbear v0.2.2 demo board to provide switching for Vref

## Schematics

Wiring diagrams.

Resistor values were calculated using https://docs.google.com/spreadsheets/d/1oWm_Bgx3GE-ziRBNUd_U12O1_qGncpa27VQ72YOOzpQ/edit?usp=sharing.  This is a type 1 amplifier circuit.

## Build Process

### Tools & Skills

What's needed to build.

### Parts Fabrication

What to do with the bill of materials.

### Assembly & Waterproofing

How to put it together.

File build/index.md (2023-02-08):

# Build

Details and instructions for building components of RRIV sondes.

### Components

* Extended Case
* Methane Sensor
* CO2 Sensor
* Temperature Sensor
* Electronics

### Use Cases

* [Methane Case 2ft](methane_case_2ft.md)
* [Methane Case 1ft](methane_case_1ft.md)
* [Methane Sensor](methane_sensor.md)
* [CO2 Sensor](co2_sensor.md)

### Templates

* [Case](template_case.md)
* [Sensor](template_sensor.md)
* [Electronics](electronics_sensor.md)

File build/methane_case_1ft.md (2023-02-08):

# Methane and Carbon Dioxide Case

Case specifically for use with the Figaro NGM2611-E13, Adafruit DHT22, AtlasScientific EZO-CO2 sensor, and an external power source.  Which informs the sensor plate, cable glands, and power supply (length of case).
[TODO: If we removed / generalized the sensor plate and cable glands requirements / instructions this could generally be for a 12" elongated case]: #

## Bill of Materials and Potential Supplier or Drawing

[columns? availability, manufacturer part number, manufacturer, notes]: #
[comment test]: #

| Item                                                       | Case Qty   | Buy Qty   |  Supplier Part # / CAD link |
| ---------------------------------------------------------- | ---------- | --------- |  -------------------------- |
| 3" ABS Schedule 40 Pipe                                    | 11"        | 10'       | [Menards 6881155 ](https://www.menards.com/main/plumbing/pipe-fittings/abs-pipe-fittings/10-abs-sch-40-plain-end-cellular-core-dwv-pipe/abs033000600hc/p-1444426392509-c-8562.htm) |
| 3" ABS Hub x Hub Coupler                                   | 2          | 1         | [Menards 6881537 ](https://www.menards.com/main/plumbing/pipe-fittings/abs-pipe-fittings/nibco-reg-hub-abs-dwv-coupling/i00975h/p-1444449159767-c-8562.htm) |
| -341 EPDM 70A O-ring                                       | 2          | 15        | [McMaster-Carr 9557K316](https://www.mcmaster.com/9557K316/) |
| 18-8 Stainless Steel Threaded Rod 3/8" -16                 | 3          | 2'        | [McMaster-Carr 98920A031](https://www.mcmaster.com/98920A031/) |
| 18-8 Stainless Steel Hex Nuts 3/8" -16                     | 24         | 100       | [McMaster-Carr 91845A031](https://www.mcmaster.com/91845A031/) |
| 18-8 Stainless Steel Washers 3/8"                          | 24         | 100       | [McMaster-Carr 92141A031](https://www.mcmaster.com/92141A031/) |
| 5" Copper Mesh/Gauze                                       | 20"        | 100'      | [McMaster-Carr 6361T16 ](https://www.mcmaster.com/6361T16/) |
| Dow Corning 111 Molykote                                   | Consumable | 5.3 Fl oz | [McMaster-Carr 1204K32](https://www.mcmaster.com/1204K32/) |
| Dessicant Packet                                           | 1          | 1000      | [McMaster-Carr 2189K34](https://www.mcmaster.com/2189K34/) |
| 11" Cable Ties                                             | 4          | 100       | [McMaster-Carr 7130K55](https://www.mcmaster.com/7130K55/) |
| Dome Cap Cable Gland 1/2" NPT .19-.35" w/ O-Ring & Locknut | 1          | 1         | [elecDirect RDC13NR](https://www.elecdirect.com/cord-grips-strain-relief/cable-glands/dome-cap-cable-gland-1-2-npt-19-35-black-complete-with-o-ring-locknut) |
| Dome Cap Cable Gland .11-.26" w/ O-Ring & Locknut          | 1          | 1         | [elecDirect RDC07AA](https://www.elecdirect.com/cord-grips-strain-relief/cable-glands/dome-cap-cable-gland-pg7-11-26-black-complete-with-o-ring-locknut) |
| 3/4" wide Velcro                                           | 1"         | 5'        | [McMaster-Carr 9273K13-9273K133](https://www.mcmaster.com/9273K13-9273K133/) |
| 18-8 Stainless Steel Phillips Flat Head #6 x 1/2" Screws   | 6          | 100       | [McMaster-Carr 90065A148](https://www.mcmaster.com/90065A148/) |
| 3/4" x 3/4" Nylon Bar                                      | 1'         | 1'        | [McMaster-Carr 8732K17](https://www.mcmaster.com/8732K17/) |
| 1/4" Clear Acrylic Lid Plate*                              | 1          | NA        | [CAD Drawing 3inch](https://github.com/rrivirr/sonde/tree/master/panels) |
| 1/4" Clear Acrylic Sensor Plate*                           | 1          | NA        | [CAD Drawing 3inch](https://github.com/rrivirr/sonde/tree/master/panels) |
| 1/4" Clear Acrylic Cage Plate*                             | 1          | NA        | [CAD Drawing 3inch](https://github.com/rrivirr/sonde/tree/master/panels) |
| ABS Cement                                                 | Consumable | NA        | [Menards  6932185](https://www.menards.com/main/plumbing/plumbing-installation-repair/pipe-cements-cleaners-primers/oatey-reg-medium-black-abs-cement-4-oz/309995/p-1444449932067-c-8530.htm?tid=-7621218153408053791&ipos=1) |

*[Flare Tech Laser & Design](https://flaretechlaser.com/)

## Diagrams

[TODO: add images to markdown file  ]:#

[insert link to diagram of entire case w/ annotations and dimensions, multiple views = top, side, bottom]:#
[Annotated Case Diagram]()
[3" Acrylic Plates CAD drawing](https://github.com/rrivirr/sonde/tree/master/panels)

## Build Process

### Tools & Skills

- [Horizontal/Vertical Metal Cutting Band Saw](https://www.harborfreight.com/horizontal-vertical-metal-cutting-bandsaw-93762.html) to cut steel threaded rod to length 
- [Reed TC4QP Tubing Cutter for plastic pipe](https://www.reedmfgco.com/en/products/plastic-pipe-tools/quick-release-tubing-cutters-for-plastic-pipe/tc4qp/) to cut ABS to length
- 2x [9/16 SAE combination wrench](https://www.mcmaster.com/56255A34/) for hex nuts
- [Milwaukee 6in Diagonal Cutting Pliers](https://www.milwaukeetool.com/Products/Hand-Tools/Pliers/Diagonal-Cutters/48-22-6106) for copper mesh and cable ties
- Measuring tape
- #2 phillips head screw driver / drill bit

### Parts Fabrication

- Cut steel threaded rod in half to 1' lengths
- Cut two 1-21/32" length sections of ABS, 20/32 to 22/32 is acceptable, too little won't hold the o-ring in place, too much won't compress the o-ring enough to seal properly
- Cut 20" of copper mesh x2
- Attach both cable glands through their respective holes in acrylic sensor plate

### Assembly & Waterproofing

1. Add cable glands to sensor plate
2. Insert ABS 1-21/32" length into each end of coupling
3. Add O-Rings around ABS
4. Add nuts & washers to rods
5. Add plates & housing to rods
6. Wrap copper mesh around sensor cage and use cable ties to hold in place

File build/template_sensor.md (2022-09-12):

# Case Title

## Bill of Materials

| Item        | Quantity    | Source URL  |
| ----------- | ----------- | ----------- |
| Glass       | 1           | https://... |
| Wire        | 20          | https://... |

## Schematics

Wiring diagrams.

### Communication protocol

### Power solution

## Diagrams

Mechanical drawings.

## Build Process

### Tools & Skills

What's needed to build.

### Parts Fabrication

What to do with the bill of materials.

### Assembly & Waterproofing

How to put it together.

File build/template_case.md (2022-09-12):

# Case Title

## Bill of Materials

| Item        | Quantity    | Source URL  |
| ----------- | ----------- | ----------- |
| Tube        | 1           | https://... |
| Wire        | 20          | https://... |

## Diagrams

## Build Process

### Tools & Skills

What's needed to build.

### Parts Fabrication

What to do with the bill of materials.

### Assembly & Waterproofing

How to put it together.

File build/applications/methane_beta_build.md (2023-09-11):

# RRIV Methane Beta Setup
## Overview
Beta version RRIV loggers with methane (CH<sub>4</sub>) and carbon dioxide (CO<sub>2</sub>). Methane sensors use a Figaro NGM2611-E13 metal oxide sensor and CO<sub>2</sub> sensors use a Atlas Scientific infrared carbon dioxide sensor. Sensors were encased in segments of 1-1/4" PVC pipe with one end covered by a 0.005" thick PTFE diaphragm to permit gas exchange with the water.

## Tools
* 2 adjustable wrench 3/8” to 1 ¼”
* Pliers 3/8” to 1 ¼”
* Mini USB to USB cable
* [Programming header](https://www.st.com/en/evaluation-tools/nucleo-f103rb.html) (Figure 1)
* ABS Rubber Cement
* [Molykote Grease 111](https://www.dupont.com/molykote.html)

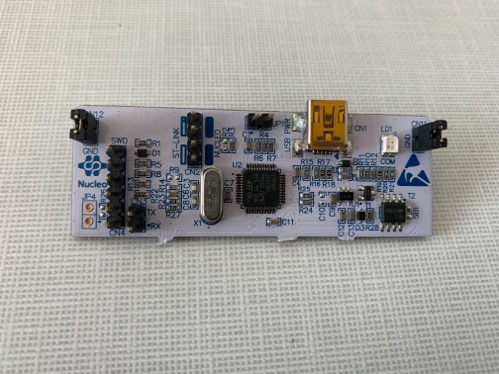
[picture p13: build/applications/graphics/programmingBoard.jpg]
Figure 1: ST Nucleo programming header


*Figure 1: ST Nucleo programming header*

## Included components
* RRIV Data Logger (V0.21)
* [Enclosed CH<sub>4</sub> sensor]()
* Enclosed CO<sub>2</sub> sensor
* ABS sonde housing

## Off the shelf components to purchase
| Item | Number Needed per Device| Source & Part Number |
| ----------- | ----------- | ----------- |
| EPDM O-Ring (Size: Dash Number 341) | 2 | [McMaster-Carr 9557K316](https://www.mcmaster.com/9557K316/) |
| 18-8 stainless steel threaded rod 3/8” – 16 [2']   | 6 | [McMaster-Carr 98804A031](https://www.mcmaster.com/98804A031/) |
| 18-8 stainless steel hex nuts 3/8” -16 | 24 | [McMaster-Carr 91845A031](https://www.mcmaster.com/91845A031/) |
| 18-8 stainless steel washers 3/8” | 24 | [McMaster-Carr 92141A031](https://www.mcmaster.com/92141A031/) |
| Tenergy rechargeable NiMH D cell batteries | 6 | [Tenergy D Cell Batteries](https://power.tenergy.com/8pcs-tenergy-centura-lite-nimh-d-1-2v-3000mah-rechargeable-batteries/) |
| Tenergy NiMH D cell battery charger | 1 | [Tenergy Battery Charger](https://www.tenergy.com/01480) |
| Dupont jumper cables F-F | 5 | [Digikey 1528-1961-ND](https://www.digikey.com/en/products/detail/adafruit-industries-llc/1950/6827084) |
| Dupont jumper cables M-M | 3 | [Digikey 1568-1512-ND](https://www.digikey.com/en/products/detail/sparkfun-electronics/PRT-12795/5993860) |
| Copper Mesh Roll | 1 | [Home Depot](https://www.homedepot.com/p/Bird-B-Gone-Copper-Mesh-20-ft-Roll-for-Rodent-and-Bird-Control-CMS-20/205862497) |

## Initial sensor setup and configuration
* Install [Microsoft VS Code](https://code.visualstudio.com/) and then from within *VS Code* install the [PlatformIO extension](https://platformio.org/).
<!-- * Go to https://github.com/rrivirr/rriv and clone the repository there with github or download manually to a folder on your computer. -->
* Go to https://github.com/kenchong48/rriv/tree/continuousPower and clone the repository there with github or download manually to a folder on your computer.
	*  If you clone the repository, you may have to navigate to the continuousPower branch, check with `git branch`, switch branches with `git checkout continuousPouwer`
* Use dupont jumper cables to connect the programming board to the RRIV logger for communication following Figures 2 and 3- programming header CN4 pins 2, 3, 4, TX, RX to the three RRIV pins 4, 3, 2 on the bottom of the board, then RX and TX on the Nucleo CN10 pins 35 and 37.
* Connect the methane sensor plugs to the board as pictured in Figure 4 - red+white into ADC4, purple+green into ADC2, black+blue+orange into ADC1. Plug the remaining 4-pin plug of the CO2 sensor into one of the ports on the back of the board.
* Plug the usb cable into the programming board and the computer you are using.
* Open VS Code and select the PlatformIO icon on the left side of the VS Code window. On the platformio home screen select `open project` and navigate to *folder* containing the RRIV repository you downloaded and select `open folder`.
* Now use the keys CTRL+SHIFT+P (macos: CMD+SHIFT+P) and type serial monitor.
	* This will present you with an option for `PlatformIO: Serial Monitor`.
	* While your computer is connected via USB to the RRIV logger is connected to a power source, select the `PlatformIO: Serial Monitor`. This will open a serial connection that will allow you to give commands to the RRIV logger.
* To learn more about the command line interface (CLI) and the commands available check RRIV documentation here or type `help` into the RRIV CLI command prompt and hit enter.
* To configure the sensor paste the following commands in the CLI one at a time (press enter after each command):<br>
&emsp;*Command for setting up sampling interval*:<br> ```set-config {"loggerName":"writeOnBoard", "siteName":"7char", "deploymentIdentifier":"15char", "wakeInterval":60, "startUpDelay":0, "burstNumber":60, "interBurstDelay":1}```<br>
&emsp;*Command that configures the humidity sensor integrated with the methane sensor:*<br>```set-slot-config {"slot":1, "type":"adafruit_dht22", "tag":"dht", "burst_size":10, "sensor_pin":5}```<br>
&emsp;*Command that configures the CO<sub>2</sub> sensor:*<br>```set-slot-config {"slot":2, "type":"atlas_co2", "tag":"atlas", "burst_size":10}```<br>
&emsp;*Command that configures the CH<sub>4</sub> sensor:*<br>```set-slot-config {"slot":3, "type":"generic_analog", "tag":"ch4", "burst_size":10, "adc_select":"external", "sensor_port":2}```

* To test the sensors type the command `start-logging` while the sensors are connected to the RRIV logger and press enter. This command will continuously report sensor values until you type `stop-logging`. Note: while the system is logging, values will continuously update sensor performance using the command start-logging. This means that when you are typing `stop-logging` the letters you type in will be broken up by new lines of data. The device will still read your typing as a single command so keep typing and press enter and the logger will stop.
* To beginning using the logger type `deploy-now` and press enter. Any time the logger is powered up after this it will immediately enter deployment mode after 5 seconds and begin collecting data following the configurations set above. Thus, you can keep the device powered down and add the batteries in the field immediately before deployment.

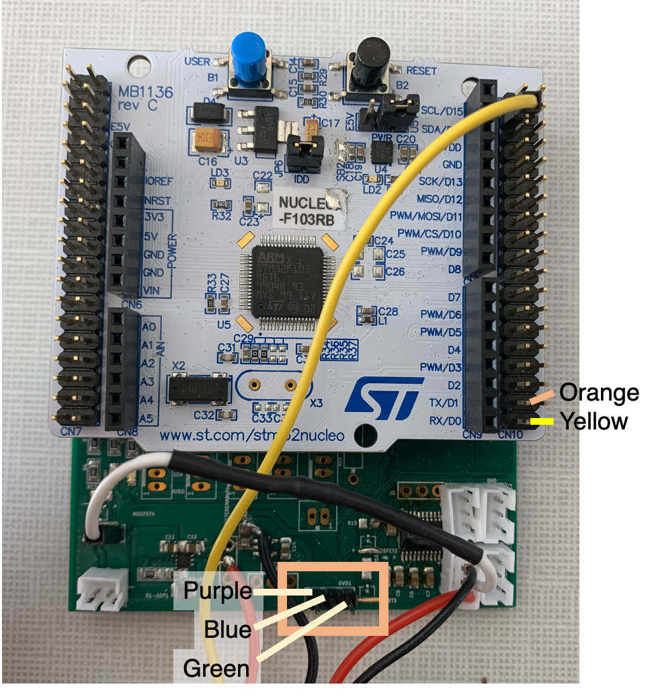
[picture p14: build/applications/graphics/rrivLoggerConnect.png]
Figure 2: RRIV Logger with the pins that are used to connect the programming board indicated by the orange box Figure 2: RRIV Logger with the pins that are used to connect the programming board indicated by the orange box. The color of the dupont jumper cable that should be connected to each pin is indicated following the color scheme used in Figure 3.


*Figure 2: RRIV Logger with the pins that are used to connect the programming board indicated by the orange box. TODO: fix annotation, order for pins is opposite, Green-Blue-Purple*

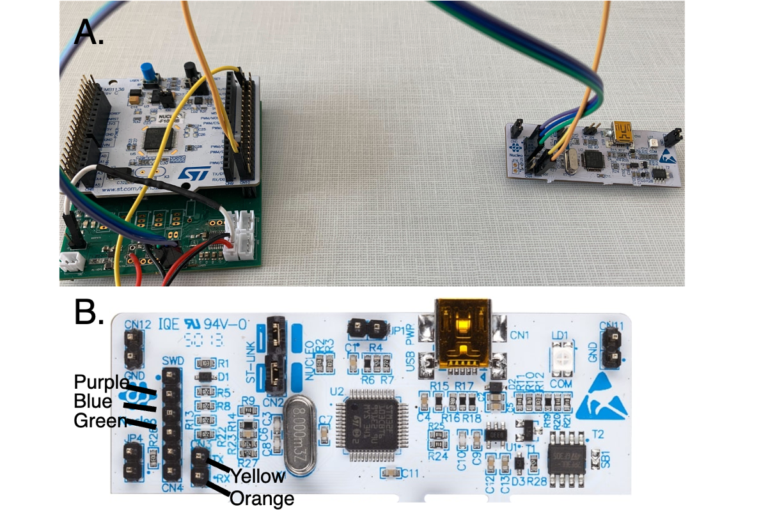
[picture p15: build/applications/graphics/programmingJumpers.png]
Figure 3: a) The programming board connected to a RRIV logger using a set of five dupont jumper cables. b) a close-up of the programming board with the color of the jumper cable to be connected at each pin indicated.


*Figure 3: a) The programming board connected to a RRIV logger using a set of five dupont jumper cables. b) a close-up of the programming board with the color of the jumper cable to be connected at each pin indicated.*

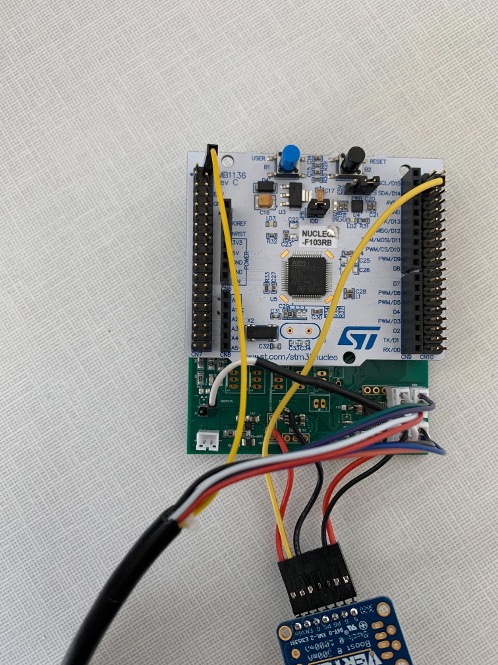
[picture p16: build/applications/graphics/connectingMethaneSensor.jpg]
Figure 4: Methane and humidity sensors plugged into the analog to digital converter (ADC) ports.


*Figure 4: Methane and humidity sensors plugged into the analog to digital converter (ADC) ports.*

## Commands and notes for rapid configuration of a device
* `get-config` is used to check the configuration of the settings as they are, the first section displayed is the datalogger settings followed by sensor slot settings
	* There is one hardcoded setting to take note of which is `continuous_power`, whether it is true/false is shown when using `get-config`.
	* To switch this setting one must go to the line `settings->continuous_power = true;` in the datalogger.cpp file and change `true` to `false`, then recompile and flash the code.
	* The instance where this should be left as `true` is when calibrating the methane sensors which benefits from taking continuous measurements and suffers from the sensor module cooling down.
* `set-config`
	* `loggerName` is a colloquial name that has been written on the back of the board in sharpie
	* `siteName` is a 7 character string to indicate where the RRIV is being deployed, this will also be used in the folder structure of CSV output, so should be unique
	* `deploymentIdentifier` is a 15 character string to indicate what experiment is being run
	* `wakeInterval` is in minutes and determines when the board wakes up to begin measurement cycles. 60 indicates to wake up every hour, 1 indicates every minute. The next interval is calculated at the end of a measurement cycle
	* `startUpDelay` is a duration in minutes to delay before starting the measurement cycle
	* `burstNumber` indicates how many burst cycles to complete during a measurement cycle
	* `interBurstDelay` now also works as an interval given in minutes for when to begin taking readings. 1 indicates to take readings at every minute
* example of set-config that will need to be customized
```
set-config {"loggerName":"writeOnBoard","siteName":"7char","deploymentIdentifier":"15char","wakeInterval":1,"startUpDelay":0,"burstNumber":60,"interBurstDelay":1}
```

* `set-slot-config`:
	* `slot` is a digital slot of data set aside in the EEPROM to hold a sensor configuration
	* `type` is what driver type occupies the slot, these can be found by looking in the registry.cpp and following the "\_TYPE\_STRING" definitions
	* `tag` is a 5 character prefix for column headers, these should be left alone unless there are multiple of the same sensor in a system
	* `burst_size` is the number of reading cycles that should occur per burst
	* `sensor_pin` only for DHT22 currently, indicates which specific GPIO pin is being used for the sensor
	* `adc_select` only for analog sensors, can be either 'internal' or 'external' and indicates whether the analog sensor data is being processed by the ADC in the MCU or the external one
	* `sensor_port` only for analog sensors, indicates which physical port the sensor is occupying
* These can and should be used as they are to setup the AHT, CO2, and CH4 sensors, though once configured should be retained:
```
  set-slot-config {"slot":1,"type":"adafruit_dht22","tag":"dht","burst_size":10,"sensor_pin":5}
```
```
  set-slot-config {"slot":2,"type":"atlas_co2","tag":"atlas","burst_size":10}
```
```
  set-slot-config {"slot":3,"type":"generic_analog","tag":"ch4","burst_size":10,"adc_select":"external","sensor_port":2}
```
* To check that all sensors are working properly use `start-logging` and when satisfied `stop-logging`
* If the DHT is showing errors restart the board using `restart` then try again
* If the serial is showing many I2C errors, disconnect the CO2 sensor and restart, if it is no longer showing I2C errors then manually switch the CO2 sensor from UART to I2C mode, if it is still showing I2C errors then unplug power and USB, hold reset button for a few seconds, then try again, or keep hitting the reset button until the errors clear
* To put the system in deployment mode use `deploy-now`, it will then go to sleep until the next wake interval

## Once the sensor has been deployed
* When the system has been recovered, if the system has been fully drained of power then disconnect the power source, if the system is still powered, hit the physical reset button (Black push button) before disconnecting power
* At this point you can remove the SD card and copy the data from it, then move folders into the oldData folder(we've been preserving old data on the SD cards for now), the file structure is `Data/{siteName}/epochTimestampAtFileCreation.CSV`
* Take the logger out of the case and connect the programming board to the device as described above (Figure 2)
* Open up the serial monitor in VS Code
* Power up the device with batteries or a wall outlet
* Once the device is fully booted up and you have reached the command prompt, you have 5 seconds to press the letter 'i' and then press enter. This puts the device back into interactive mode for further use

## Data
* The DHT22 reports temperature in degrees Celsius and relative humidity in percentage
* CO2 data is reported in ppm
* Methane data is reported as a digital reading, which can be converted to volts by `reading*5/4096` or millivolts `reading*5000/4096`, 5V being the voltage to the ADC and sensor, and 4096 being 2^12, which is the precision of the ADC

## Sonde assembly
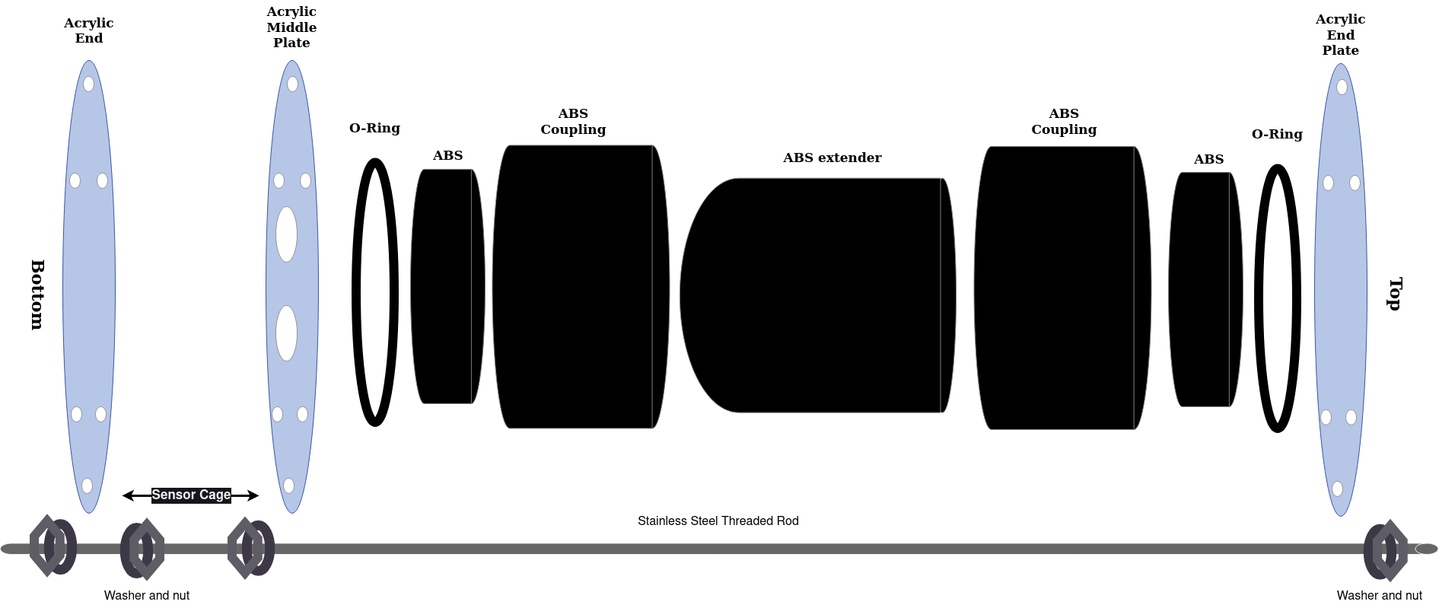
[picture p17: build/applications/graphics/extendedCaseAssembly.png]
Figure 5: Assembly of the extended sensor housing

*Figure 5: Assembly of the extended sensor housing*

* Part assembly: 
	* Use the ABS cement to secure the central housing ABS section into both the open sides of the couplers. Follow directions on the ABS cement to do so. Leave to cure in a ventilated space for 2hours
	* Apply a coat of Molykote 111 around the large O-rings and add them around the short sections of ABS in the couplers

### Case Assembly:
1. Add 2 nuts onto each of the 6 steel threaded rods, around 1" and 8" from the same end, then add washers to them one from each end of the rod.
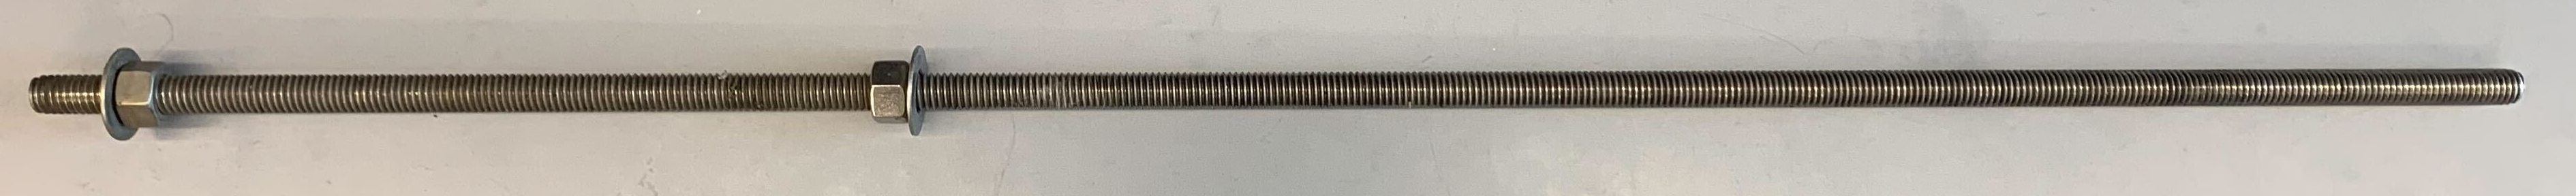
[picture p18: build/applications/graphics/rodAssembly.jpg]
steel threaded rod assembly

2. Add the 6 rods through an acrylic end plate (does not have the holes for the cable glands / sensors) and affix each rod with another washer and nut.
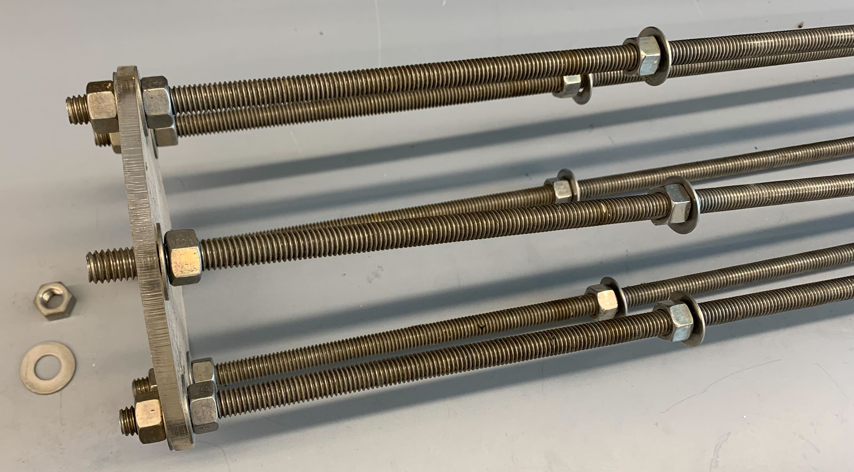
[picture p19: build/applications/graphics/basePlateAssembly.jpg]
base plate assembly

3. Apply Molykote to the O-ring of the cable gland and attach with sensors through the sensor plate, hand tighten or use pliers. If the O-ring is displaced the it is too tight.
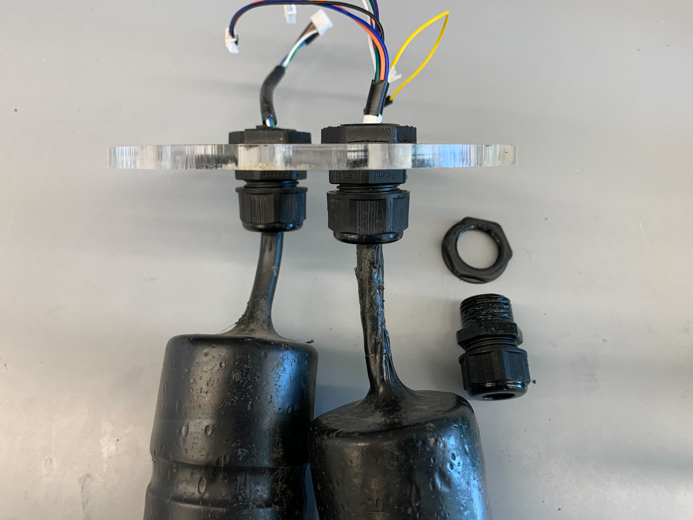
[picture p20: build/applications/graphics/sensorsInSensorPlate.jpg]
sensors in sensor plate

4. Rest the sensor plate on the open set of washers and visually level the nuts as best as possible, the goal is to keep the plate flat.
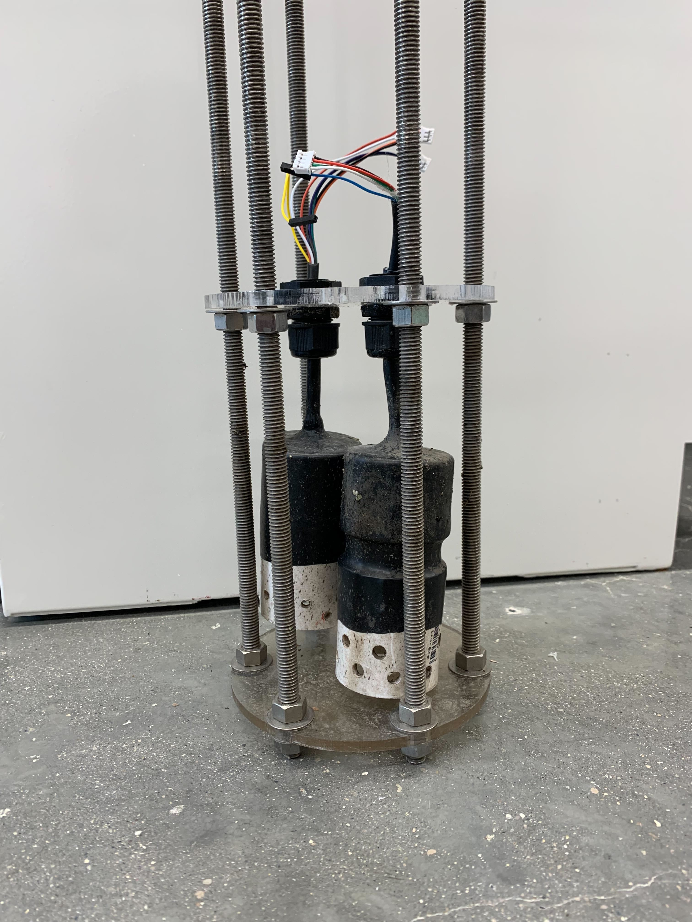
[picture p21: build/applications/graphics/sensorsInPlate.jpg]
sensor plate assembly

5. If deploying follow next steps, if doing a submersion test, proceed directly to sealing.

### Deploying:
1. Add RRIV board to battery assembly using Velcro.
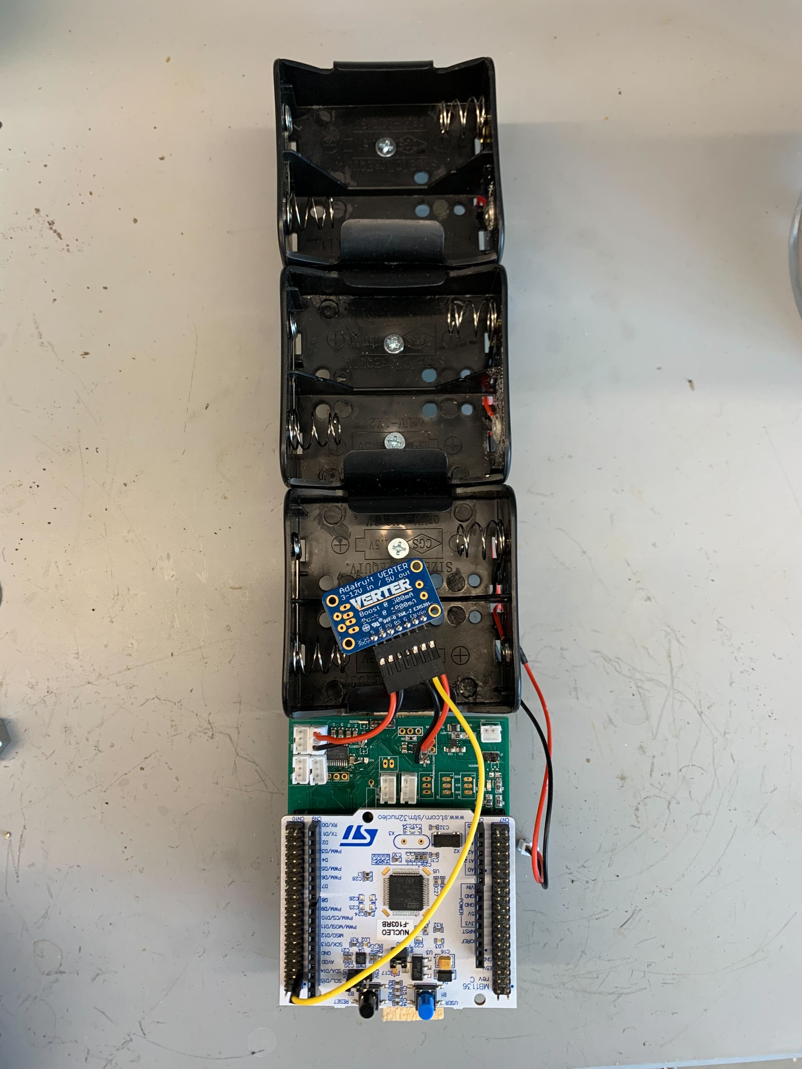
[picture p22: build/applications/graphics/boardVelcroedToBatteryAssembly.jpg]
board velcroed to battery assembly

2. Place board + battery assembly into center of rods, taking care to ensure no wires go around the rods. Then orient so that the dowel rod can sit flat on the acrylic plate and connect the sensors.
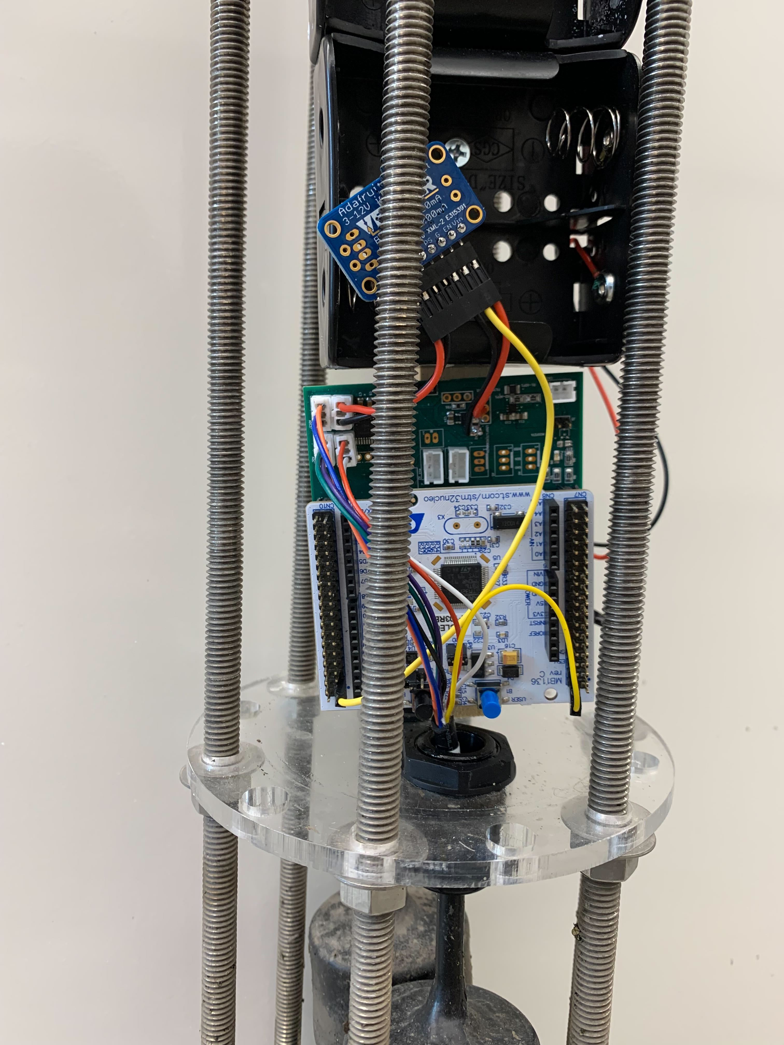
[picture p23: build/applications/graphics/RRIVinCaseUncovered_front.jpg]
Front

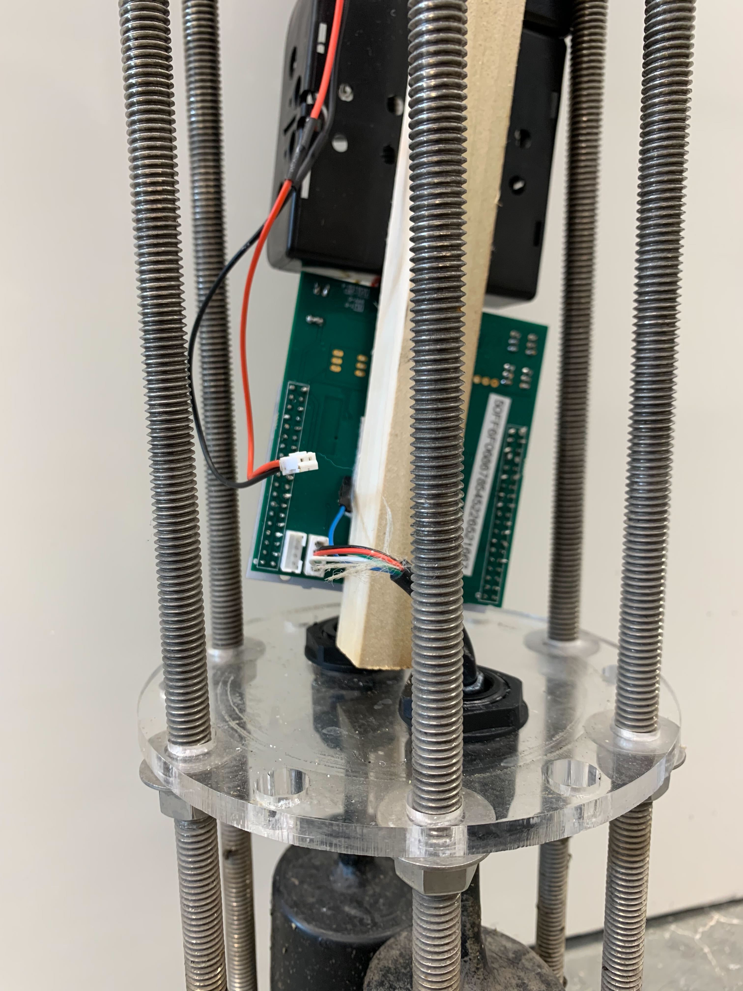
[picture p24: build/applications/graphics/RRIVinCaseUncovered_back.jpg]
Back

3. Set RRIV board to deployment mode by connecting to serial, checking sensors are working using `start-logging` (`stop-logging` when done checking), then using the command `deploy-now`.
4. Slide housing around the assembly, check for wires trapped underneath, mainly the blue wire of the CO2 sensor, then add dessicant pack in from the top.
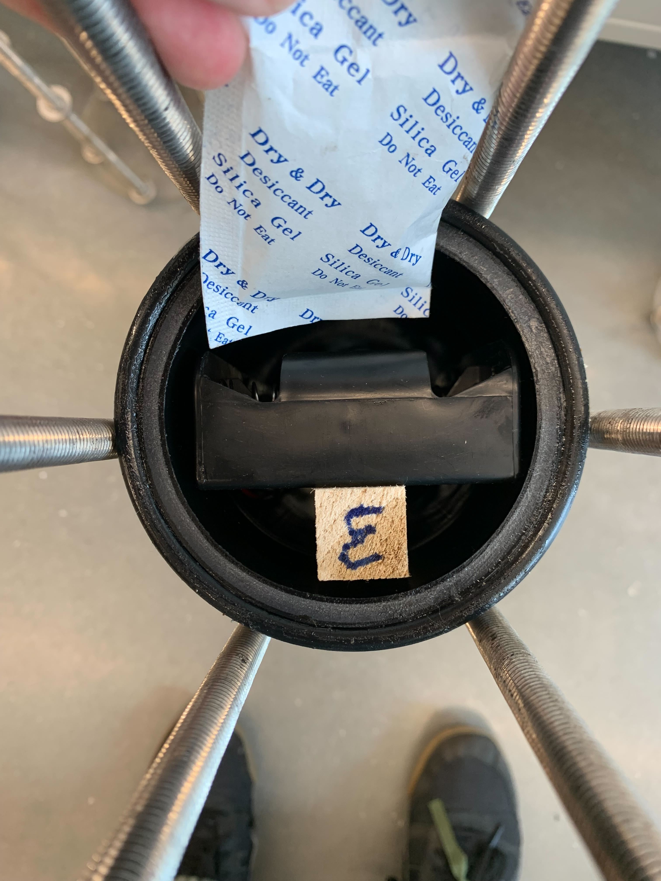
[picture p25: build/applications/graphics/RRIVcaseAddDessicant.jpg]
Add dessicant add dessicant

5. Wrap copper mesh around the sensor cage and affix with cable ties.
6. Proceed to sealing

### Sealing:
1. Add top plate and hand tighten washers and nuts onto each rod.
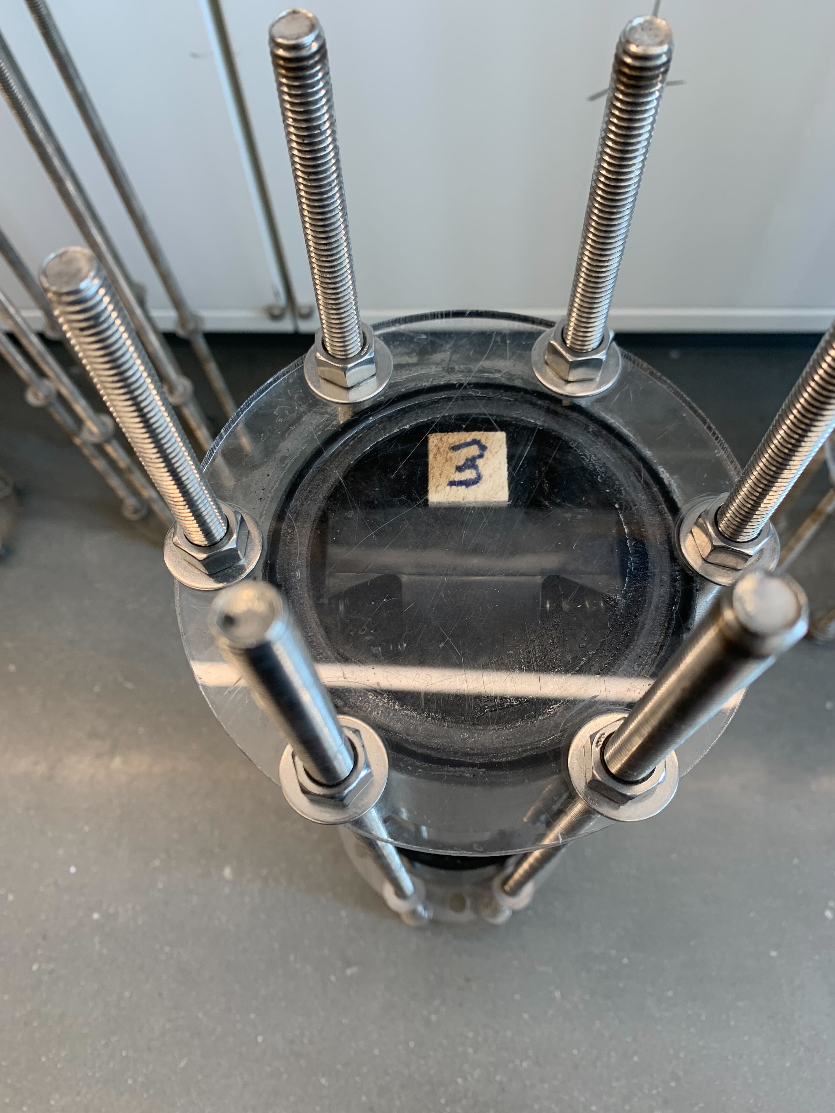
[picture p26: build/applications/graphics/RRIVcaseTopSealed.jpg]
seal top

2. Make one round of tightening the nuts in pairs across from each other using one or two sets of pliers, making ~180 degree turns and hand tightening the other nuts after each pair. 
3. Hand tighten the nuts on the sensor plate up towards the top plate, then repeat step 4.
4. Check each top nut by trying to make a 90 degree turn on each, they should all feel similarly tight.
5. Visually check the seal formed on the O-ring against the acrylic plate, you should not see the O-ring deform or have anything trapped underneath it, restart if you do.

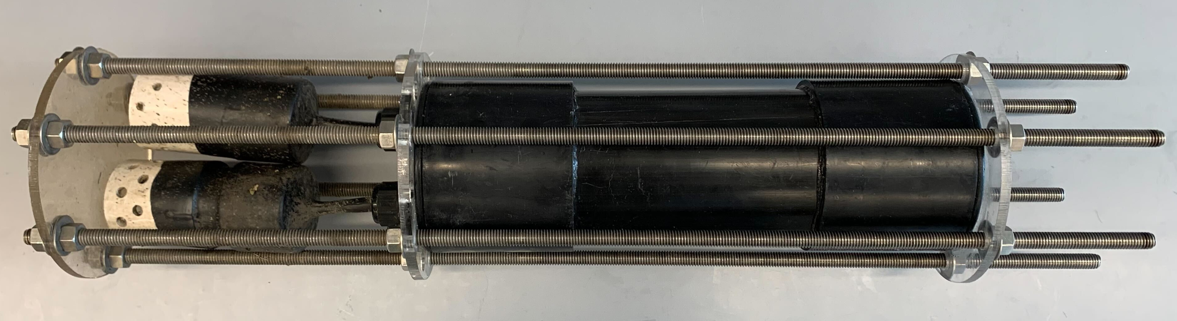
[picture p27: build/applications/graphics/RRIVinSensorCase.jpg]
Figure 6: RRIV in extended sensor housing

*Figure 6: RRIV in extended sensor housing*

### Submersion tests (conducted without RRIV electronics in case):
* 30 minutes and 1 hour are good checking points for initial leaks. 24 hours for next day.
* In the event of a severe leak during testing, check sensor cases have not also flooded which can happen if the water traverses through the wires/cables of the sensor. If they have flooded, the PTFE should be cut to allow the case to drain, then dried; sensor cases can be remade if the sensors are still functioning. Otherwise, allow sensor cables to dry fully before using them.

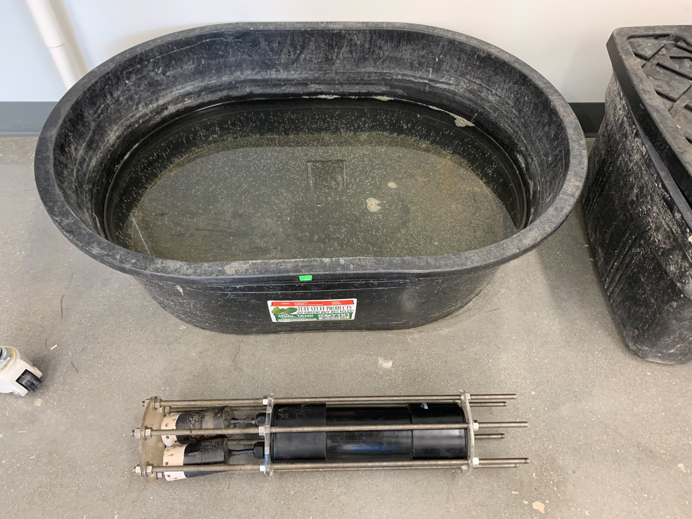
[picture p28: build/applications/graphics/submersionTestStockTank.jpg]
Stock tank submersion Submerge horizontally in a stock tank and weigh down the main housing to test the entire case

*Submerge horizontally in a stock tank and weigh down the main housing to test the entire case*

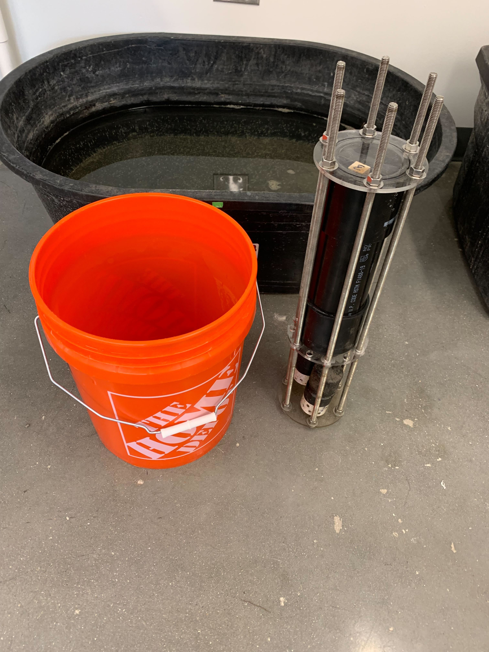
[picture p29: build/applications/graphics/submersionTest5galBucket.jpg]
5gal bucket submersion test Submerge vertically in a 5gallon bucket to test just the sensor plate

*Submerge vertically in a 5gallon bucket to test just the sensor plate and cable glands*

<!-- ![x](graphics/x.jpg "x") -->

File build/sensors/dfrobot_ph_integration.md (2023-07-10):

# DF Robot Analog pH Sensor

## Parts needed
* [DFRobot pH Sensor](https://www.dfrobot.com/product-1782.html)
* M20 IP67 Cable Gland (Supplier: [Elecdirect Dome Cap Cable Gland](https://www.elecdirect.com/cord-grips-strain-relief/cable-glands/dome-cap-cable-gland-m20-19-35-black-complete-with-o-ring-locknut))
* Lithium Moly Grease (e.g., [Lucasoil Lithium Grease](https://www.amazon.com/Lucas-Oil-10533-Lithium-Grease/dp/B004X70LZA/ref=asc_df_B004X70LZA/?tag=hyprod-20&linkCode=df0&hvadid=312151168520&hvpos=&hvnetw=g&hvrand=12751387308192042965&hvpone=&hvptwo=&hvqmt=&hvdev=c&hvdvcmdl=&hvlocint=&hvlocphy=9011858&hvtargid=pla-364752123727&th=1))
* 22 AWG hook0up wire (e.g., [Adafruit 22AWG Spool Set](https://www.adafruit.com/product/3175?gclid=Cj0KCQiA95aRBhCsARIsAC2xvfzUefNXaZgFmL8MpqskC52_lq_Huy3KYFDuIzKR2XJ_EnG1sNZSfuQaAtqzEALw_wcB))
* [Female 3-pin JST-PH plugs with crimp pins](https://www.amazon.com/CQRobot-Connector-Terminal-Industrial-Integrated/dp/B0731MZCGF)

## Hardware Integration
### Connectivity
* A cable must be built or modified to provide connectivity between the RRIV board and the Gravity analog pH meter. A female 3-pin JST-PH plug should be used for the end connecting to the pH meter. If using a RRIV v0.3 board, a female 3-pin JST-PH plug should be used for the end connecting to the RRIV board. For a RRIV v0.4 board, a female 3-pin _JST-XH_ plug should be used.
* Note: the sequence of pins on the RRIV and pH meter boards differ (see Figure 1). Construction of the cable should should follow the details in Figure 2

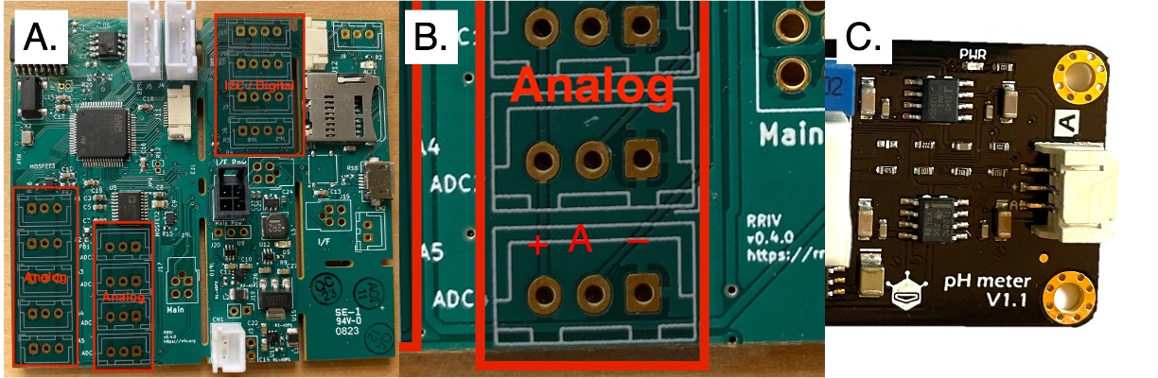
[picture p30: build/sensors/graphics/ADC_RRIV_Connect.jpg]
Figure 1: Connecting Gravity analog sensors to the analog to digital converter (ADC) ports. A) RRIV V0.4 board with ADC interfaces indicated; B) Close-up of RRIV ADC interfaces indicating connection configuration; C) Glose up of Gravity pH meter interface. Note the sequence of pins for this connect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 Figure 1: Connecting Gravity analog sensors to the analog to digital converter (ADC) ports.

**Figure 1:** Connecting Gravity analog sensors to the analog to digital converter (ADC) ports. A) RRIV V0.4 board with ADC interfaces indicated; B) Close-up of RRIV ADC interfaces indicating connection configuration; C) Glose up of Gravity pH meter interface. Note the sequence of pins for this connector differs from the sequence on the RRIV board.

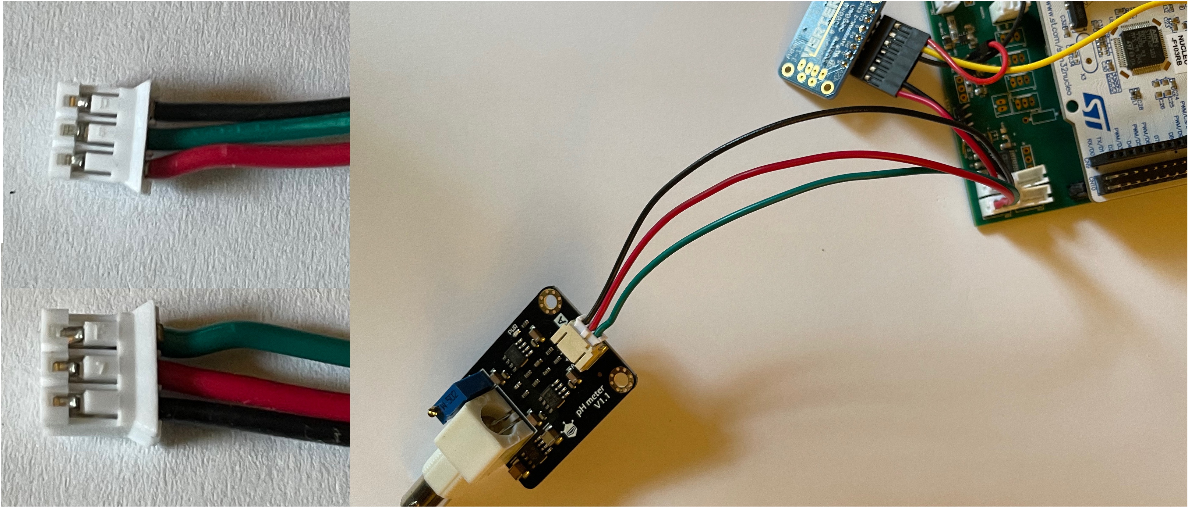
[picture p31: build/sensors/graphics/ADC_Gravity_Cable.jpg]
Figure 2: Connecting Gravity analog sensors to the analog to digital converter (ADC) ports with closeup views of the cables used for connecting.

**Figure 2:** Connecting Gravity analog sensors to the analog to digital converter (ADC) ports with closeup views of the cables used for connecting.

### Case integration
* The pH sensor is mounted into the sensor plate of the RRIV logger case using a M20 IP67 cable gland (Figure 3).
* Apply lithium moly grease to the cable gland to help ensure a water-tight seal and preserve the life of the cable gland.

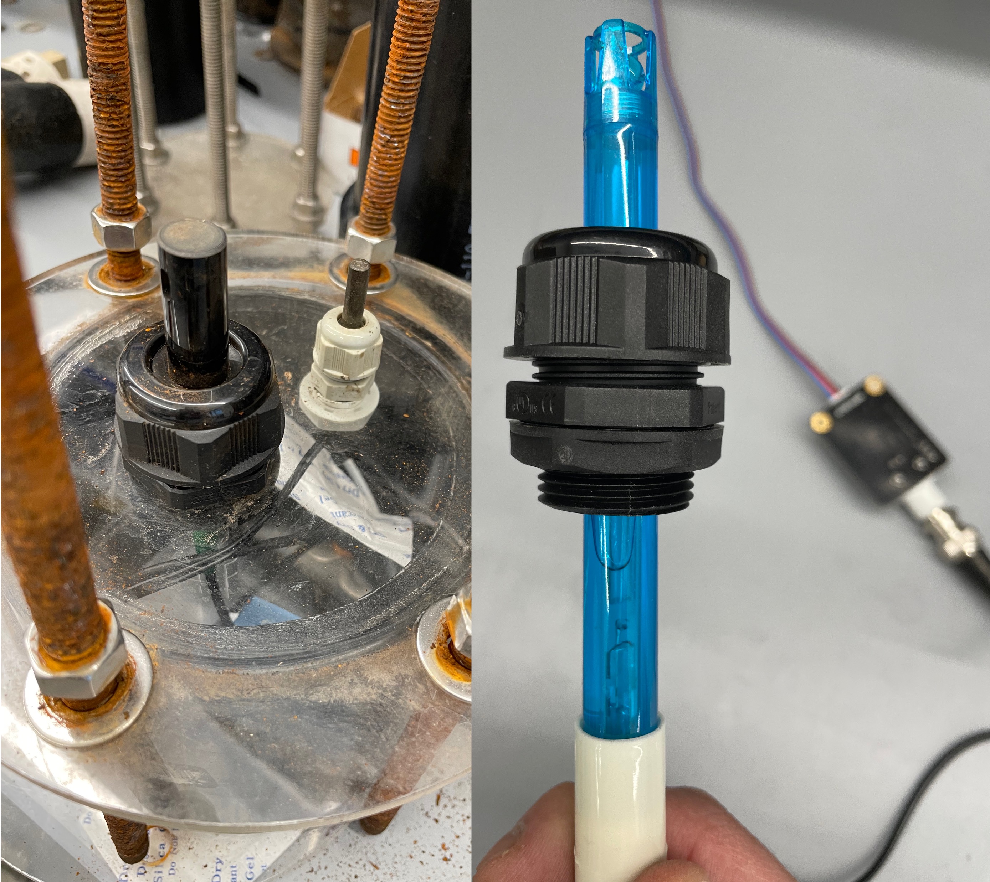
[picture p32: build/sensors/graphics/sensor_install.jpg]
Figure 3: Images showing how the pH sensor is mounted in the sensor plate. Figure 3: Images showing how the pH sensor is mounted in the sensor plate

**Figure 3:** Images showing how the pH sensor is mounted in the sensor plate

## Application and CLI Use
### Initial Setup
* Works with the _generic_analog_driver_.
* The command `set-slot-config` is used to configure a sensor for use with the RRIV logger:
	* `slot` is a digital slot of data set aside in the EEPROM to hold a sensor configuration
	* `type` is what driver type occupies the slot, these can be found by looking in the registry.cpp and following the "\_TYPE\_STRING" definitions
	* `tag` is a 5 character prefix for column headers, these should be left alone unless there are multiple of the same sensor in a system
	* `burst_size` is the number of reading cycles that should occur per burst
	* `sensor_pin` only for DHT22 currently, indicates which specific GPIO pin is being used for the sensor
	* `adc_select` only for analog sensors, can be either 'internal' or 'external' and indicates whether the analog sensor data is being processed by the ADC in the MCU or the external one
	* `sensor_port` only for analog sensors, indicates which physical port the sensor is occupying
* These can and should be used as they are to setup the AHT, CO2, and CH4 sensors, though once configured should be retained:
```
  set-slot-config {"slot":1, "type":"generic_analog", "tag":"pH", "burst_size":10, "adc_select":"external", "sensor_port":2}
```
* `get-config` is used to check the configuration of the settings as they are, the first section displayed is the datalogger settings followed by sensor slot settings
* The command `set-config` is used to configure sensors and sampling parameters.
	* `loggerName` is a colloquial name that has been written on the back of the board in sharpie
	* `siteName` is a 7 character string to indicate where the RRIV is being deployed, this will also be used in the folder structure of CSV output, so should be unique
	* `deploymentIdentifier` is a 15 character string to indicate what experiment is being run
	* `wakeInterval` is in minutes and determines when the board wakes up to begin measurement cycles. 60 indicates to wake up every hour, 1 indicates every minute. The next interval is calculated at the end of a measurement cycle
	* `startUpDelay` is a duration in minutes to delay before starting the measurement cycle
	* `burstNumber` indicates how many burst cycles to complete during a measurement cycle
	* `interBurstDelay` now also works as an interval given in minutes for when to begin taking readings. 1 indicates to take readings at every minute
* example of set-config that can be further customized. This command sets up a logger named "writeOnBoard" that will wake up after sleeping for 1 minute with 
```
set-config {"loggerName":"writeOnBoard", "siteName":"7char", "deploymentIdentifier":"15char", "wakeInterval":1, "startUpDelay":0, "burstNumber":60, "interBurstDelay":1}
```
* To check that all sensors are working properly use `start-logging`. This will display sensor readings at continuous intervals. You can evaluate the readings to confirm the sensor is operating properly. When you are done with this process type the command `stop-logging`. Data will continue logging so the keystrokes you type may become separated, but the command will register if you type the entire command and press enter. The data can be offloaded from the SD card to confirm that data collection was satisfactory.

### pH sensor calibration
* Calibration values are entered manually.
* Begin by typing the command `start-logging`. This will provide a continuous read of raw pH values in millivolts.
* While the sensor is logging, place hte sensor in the first calibration solution.
  * Once the raw voltage measurements have stabilized, record the pH of the calibration solution and the corresponding millivolt value of the sensor.
* Repeat the above step for one or two different other pH calibration solutions.
* Use the `calibrate` command to record the calibration values for the sensor. Each calibration point is entered with the following command, which has three values associated with it.
  * <calibrate> [sensor slot #] [step] [value]
  * The first value, `sensor slot #`, is the slot number previously assigned (in this example slot 1 was used).
  * The second value, `step`, is the pH of the calibration solution.
  * The third value, `value`, is the raw analog reading in millivolts obtained by the sensor.
* Repeat the step above for all 3 calibration points.

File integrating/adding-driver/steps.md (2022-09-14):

# Steps
The driver class creation script will create a .h file with all necessary variables and functions to define the class, and a .ccp file that contains stubs for all functions that need to be implemented.  Implementing a driver thus then proceeds by writing logic into the function stubs in the .cpp file, and no modifications to the generated .h file are necessary except where explicitly described in this document.

The new C++ class file created by the driver template script contains the complete skeleton of variables and functions needed to create a working driver for your sensor.  However, some functions and variables will need to be updated to complete the implementation of the driver.  Other functions and variables only need to be updated to implement optional features.  There are also functions and variables that do not need to be updated at all, they are just part of the driver skeleton code itself.

An approach to updating necessary functions and variables should proceed as follows:
1. Implement sensor setup and measurement functionality.
2. Implement data output functionality.
3. Implement sensor specific configuration functionality (optional).
4. Implement callibration functionality (optional).

## Implement sensor setup and measurement functionality.

Sensor setup and measurement functionality is implemented by updating the following functions:
1. setup()
2. stop()
3. isWarmedup()
4. takeMeasurement()

### setup()

The *setup()* function should preform any logic that is needed to start collecting readings from the sensor.  An analog sensor typically has no setup logic.  iDigital sensors, such as I2C, SPI, or GPIO protocol sensors, often _will_ have commands that must be sent to them to start collecting readings, or select certain functionality.  Details on this can be found in the documentation for the sensor being integrated.  This logic all goes in the setup() function.

### stop()

*stop()* is called for each sensor right before the datalogger goes to sleep between measurement cycles.  Some digital sensors have specific logic for halting readings, or have specific low power modes.  Any related logic from the sensor's documentation should be implemented in the stop() function.

### isWarmedUp()

`isWarmedUp()` returns a boolean value, indicating if the sensor is ready to start returning values.  `isWarmedUp()` is called after *setup()*, and the datalogger will wait for *isWarmedUp()* to return true before starting to read measurements from the sensor.  The logic of *isWarmedUp()* will typically be a time delay or  command that checks with a digital sensor for readiness.  More advanced implementations might look at a standard deviation of returned values, such as for an analog sensor.

### takeMeasurement()

This function attempts to take a single measurement from the sensor, and returns true or false depending on if the measurement was successfully taken.  Additionally, this function must save the measurement value into the *this.value* and add this value into the burst summary calculation logic.  In the case where a sensor returns multiple variable, the class must be updated to provide private storage for as many variables as necessary and all must be populated on a successful sensor read. To update the class with the appropriate private storage variables, go to the .h file and define the appropriate value variable or variables in the private storage class.

Burst summary calculation is the mechanism by which multiple readings during a burst are combined to produce a single reading, typically a mean value.  addValueToBurstSummaryMean(tag, value) is used to track these values and later produce a mean.  To use this function in takeMeasurement, use a #define to define a tag for each variable returned by the sensor, and call addValueToBurstSummaryMean with this tag in the first parameter and a measuremented value in the second parameter for each variable measured successfully by the sensor.

## Implement data output functionality.
Data output to the SDCard is implemented by updating the following functions:
1. `getRawDataString()`
2. `getSummaryDataString()`

Additionally, the following privet instance variables must be updated:
1. `baseColumnHeaders`
2. `dataString`

### getRawDataString()

This function simply returns a comma delimited string of the values stored by the last successfully reading from the sensor.  This is typically done by using sprintf to print into character array, and then returning this character array.  Such as the following code snipped for a single variable.  Using the instance variable dataString for storage allows a char * to be returned without concerns about storage scope.  

```
sprintf(dataString, "%d",value);
return dataString;
```

### getSummaryDataString()

This function is similar to `getRawDataString()` execpt that instead of returning values from the last successful sensor reading, it returns a summary value for a burst cycle.  This is typically a mean value, which can be retrieved from the values stored by `addValueToBurstSummaryMean(tag, value)` by using the function `getBurstSummaryMean(tag)`.  `getBurstSummaryMean(tag)` must be called with the appropriate tag for each variable returned by the sensor.  The return value from `getSummaryDataString()` is a comma delimited list of a summary value for each variable returned by the sensor.

For advanced use cases, summary logic other than a mean value may be desired, in which case it is left to the developer to implement appropriate storage and summarization functions in the driver class to support this feature.

### baseColumnHeaders

The baseColumnHeaders private variable stores a const value that contains a comma delimited list of the column header strings for each variable returned by the sensor.  If a sensor returns a single, uncalibrated value then this variable will just contain a single variable name such as `const char *baseColumnHeaders = "value";`.  When both a raw and calibrated value are returned, a string such the following can be used `const char *baseColumnHeaders = "raw,cal";`.  For more complex sensors as many column headers as necessary should be included, such as const char `const char *baseColumnHeaders = "temperature,humidity,CO2";`.  Note that drivers are also configured with a prefix tag that will be added to each of these column headers for each instantiaion of the driver.

### dataString

`dataString` is a private variable used to temporarily stored returned output from the sensor during output to the SDCard.  The size of this character array must be increased to account for the largest possible number of characters that `getRawDataString()` or `getSummaryDataString()` could need to write for output.

## Implement sensor specific configuration functionality (optional).

Not all sensors will have specific configurations beyond what is provided by the sensor driver superclass already, but many will.  To implement these configurations and expose them over the CLI, the following functions and the driver_configuration struct must be updated.

1. configureSpecificConfigurationsFromBytes(...);
2. getDriverSpecificConfigurationBytes();
3. configureDriverFromJSON(...);
4. appendDriverSpecificConfigurationJSON(...);
5. setDriverDefaults();

## Implement callibration functionality (optional).

## Style Guide
For C++ variable naming and other style conventions, reference the [Google C++ Style Guide](https://google.github.io/styleguide/cppguide.html).
Variable naming reference:
* Class names use studly caps (e.g., StudlyCaps).
* Variable and function names use camel caps (e.g., camelCaps).
* Preprocessor macros (e.g., for use with #define) use screaming snake case (e.g., SCREAMING_SNAKE_CASE).

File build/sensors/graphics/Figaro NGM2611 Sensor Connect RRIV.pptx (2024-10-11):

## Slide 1

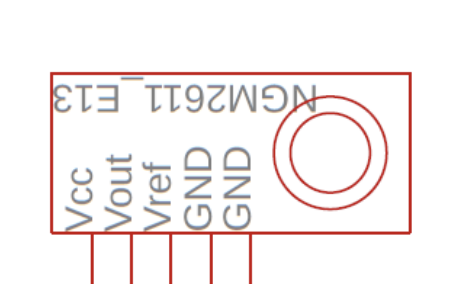
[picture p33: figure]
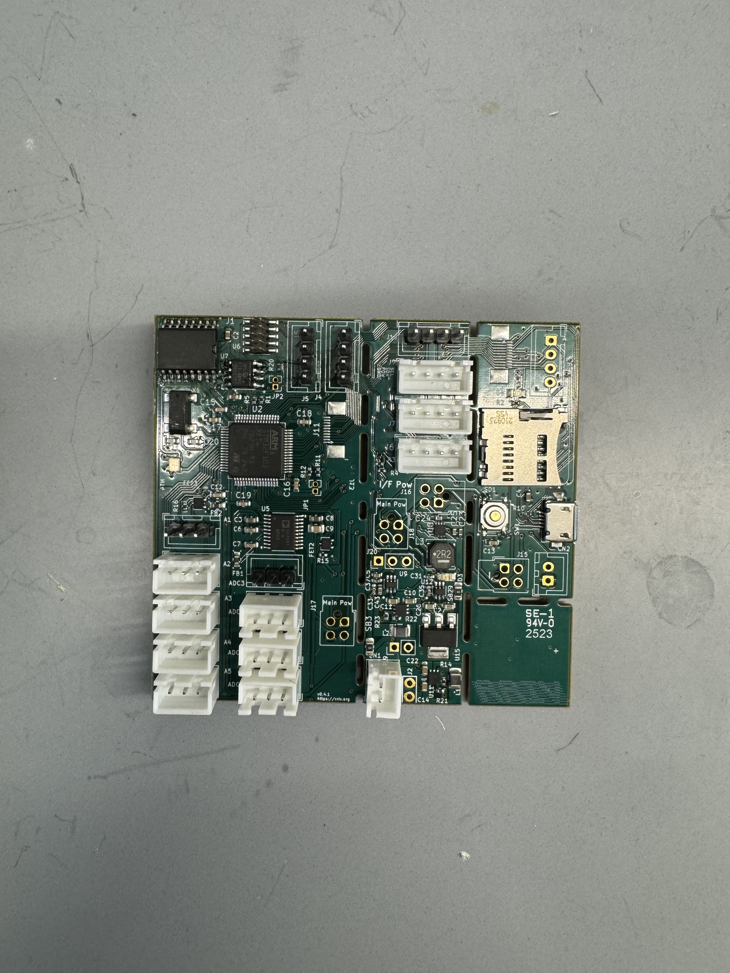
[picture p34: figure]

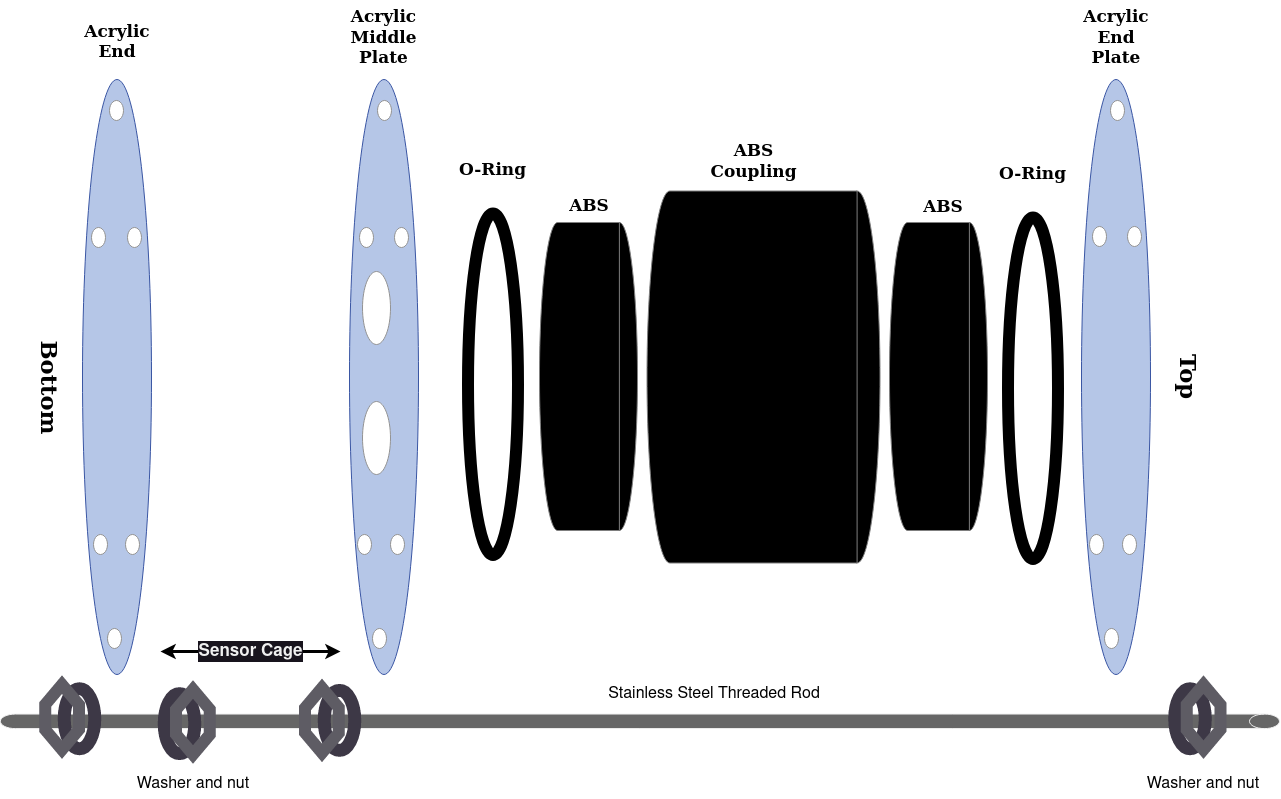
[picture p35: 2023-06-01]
build/applications/graphics/caseAssembly.png

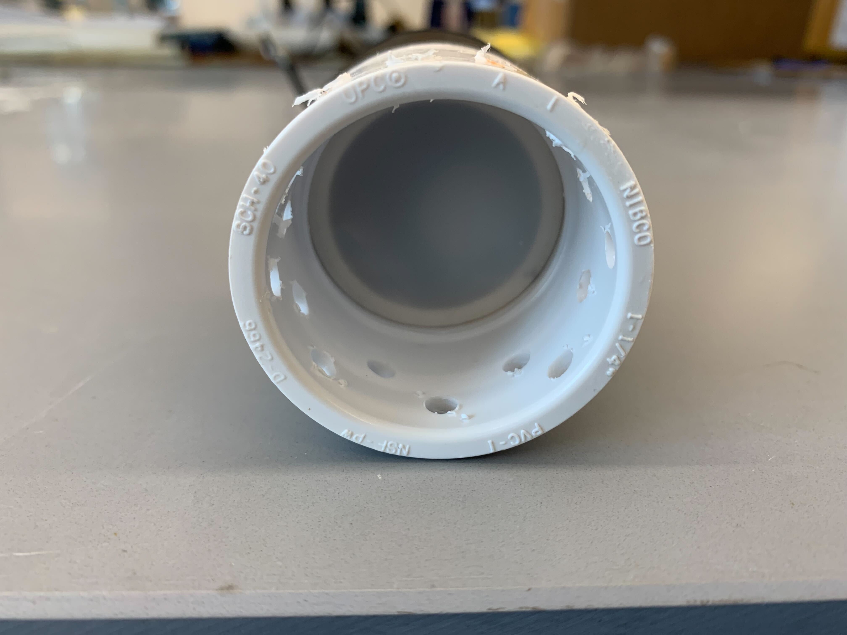
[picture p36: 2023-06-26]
build/applications/graphics/ch4co2case_membrane.jpg

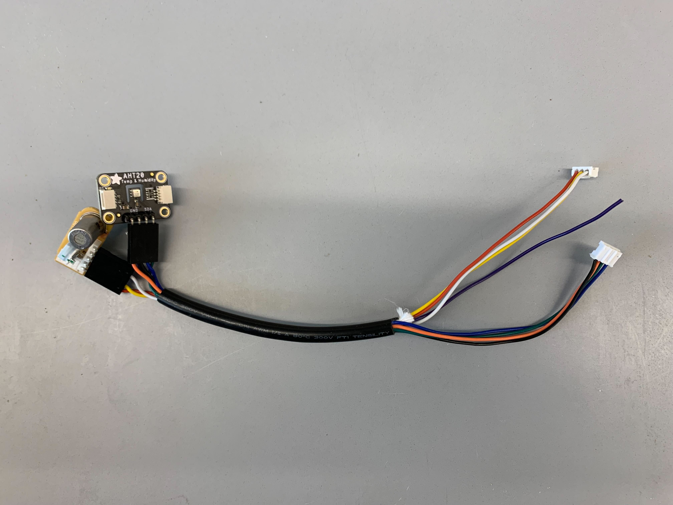
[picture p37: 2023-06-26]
build/applications/graphics/ch4aht20_full.jpg

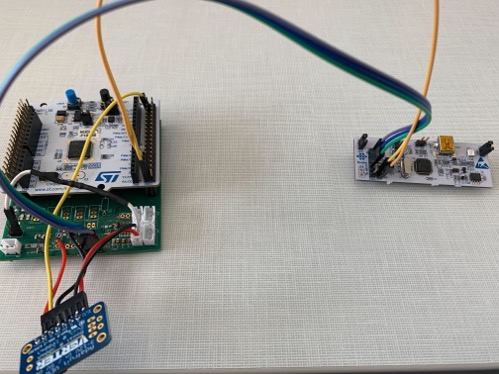
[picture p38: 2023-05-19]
build/applications/graphics/connectingProgrammingBoard.jpg

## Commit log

2022-09-12 Add template for sensor build
2022-09-12 Add sensors
2022-09-13 fix: add flaretech laser as a suggesttion for acrylic plates
2022-09-15 feat: add methane sensor, modify methane case slightly
2022-12-13 update methane sensor, add co2 sensor, split methane case into 2ft and 1ft design
2023-05-31 Update methane_beta_build.md
    extending configuration commands for deployment with explanations of items in the json, adding section for units for sensors being deployed
2023-06-06 Update methane_case_2ft.md
    adding 2 d battery holders, and notes on ABS pipe measurements
2023-06-19 Create CLI_commands_v1.md
    current cli commands
2023-06-22 docs: usb power
2023-06-22 docs: battery power
2023-06-26 docs: sensor and case build steps
    [BackPanel.dxf, SensorPanel.dxf]
2023-06-26 Add files via upload
    dht22 + methane sensor
    aht20 + methane sensor
    atlas co2 sensor, unmodified
    cases
2023-07-08 docs: add some sensor details
2023-07-10 adding sensor graphics
2023-11-29 Add some datasheet s for the groundwater flow sensor
2024-10-11 adding methane wiring sketch
2024-11-15 fixing wiring diagram
